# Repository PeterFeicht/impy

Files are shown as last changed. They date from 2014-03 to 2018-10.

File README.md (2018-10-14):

Bachelor's Thesis
=================

This project contains all of the stuff from my [bachelor's thesis](thesis.pdf).

The goal is to create an impedance spectrometer based on the
*Impedance Converter Network Analyzer* chip [AD5933][1] from Analog Devices.

The device uses an [STM32F4 Discovery board][2] by ST for interfacing with a PC
and MATLAB for controlling the measurement parameters.

[1]: http://www.analog.com/en/digital-to-analog-converters/direct-digital-synthesis-dds/ad5933/products/product.html
    "Analog Devices product page"
[2]: http://www.st.com/stm32f4-discovery "ST product page"
[3]: http://www.ti.com/tool/tmdssk3358 "TI product page"

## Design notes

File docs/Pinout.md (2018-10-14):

# Discovery Board Main Shield Pin Usage

This is the preliminary pin usage plan for the main shield.

Components on the main shield (most of them optional) are:

 + AD5933
 + Analog front end
 + EEPROM
 + Ethernet MAC
 + SPI Memory
 + USB A Connector

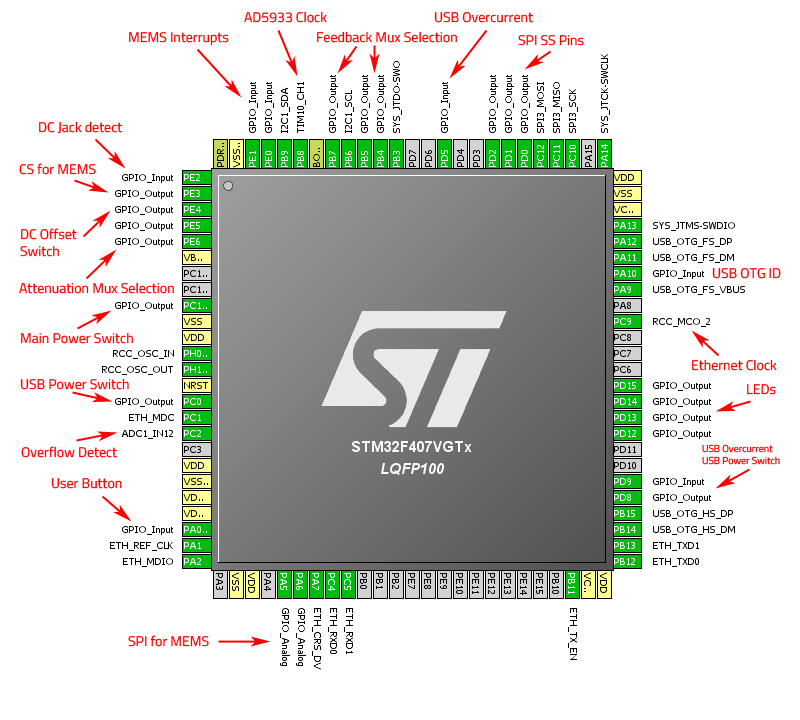
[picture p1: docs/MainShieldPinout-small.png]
Used pins for the main shield


## Pin Description:

Description of the used pins, clockwise from PE1:

| Pin(s)     | Function                  | Description                                                                 |
| ---------- | ------------------------- | --------------------------------------------------------------------------- |
| PE0/1      | MEMS Interrupt            | Unused, see [DiscoveryPins](DiscoveryPins.md).                              |
| PB9        | I2C Data                  | Used for communication with AD5933 and EEPROM.                              |
| PB8        | AD5933 Clock              | Low speed clock signal for the AD5933 for low frequency measurements.       |
| PB7        | Feedback Mux Selection    | Analog mux input selection signals, feedback resistor mux.                  |
| PB6        | I2C Clock                 | Used for communication with AD5933 and EEPROM.                              |
| PB5/4      | Feedback Mux Selection    | Analog mux input selection signals, feedback resistor mux.                  |
| PB3        | SWD Trace                 | Not used on the shield.                                                     |
| PD5        | USB Overcurrent           | Unused, see [DiscoveryPins](DiscoveryPins.md).                              |
| PD2..0     | SPI SS Pins               | Pins to be used for SPI device selection.                                   |
| PC12..PC10 | SPI Interface             | Used for SPI devices: SRAM, Flash and input Mux.                            |
| PA14/13    | SWD Clock and Data        | Not used on the shield.                                                     |
| PA12..PA9  | USB Device                | Discovery USB, not used on the shield.                                      |
| PC9        | Ethernet Clock Out        | 50MHz clock output to be used by the Ethernet MAC and STM32 ETH peripheral. |
| PD15..PD12 | LEDs                      | Discovery LEDs, not used on the shield.                                     |
| PD9        | USB Overcurrent           | Overcurrent signal for the USB host port.                                   |
| PD8        | USB Power Switch          | Output power switch enable signal for the USB host port.                    |
| PB15/14    | USB Host                  | Used for the USB A (host) connector on the shield.                          |
| PB13..PB11 | Ethernet TX               | Transmit data and enable pins for the Ethernet MAC.                         |
| PC5/4      | Ethernet RX               | Receive data pins for the Ethernet MAC.                                     |
| PA7        | Ethernet CS/DV            | Carrier Sense/Data Valid pin for the Ethernet MAC.                          |
| PA6/5      | SPI for MEMS              | Unused, see [DiscoveryPins](DiscoveryPins.md).                              |
| PA2        | Ethernet MDIO             | Management data pin for the Ethernet MAC.                                   |
| PA1        | Ethernet Clock In         | Reference clock signal input for the Ethernet MAC.                          |
| PA0        | User Button               | Discovery Button, not used on the shield.                                   |
| PC2        | Overflow Detect           | ADC input to detect possible AD5933 clipping for auto-ranging.              |
| PC1        | Ethernet MDC              | Management clock pin for the Ethernet MAC.                                  |
| PC0        | USB Power Switch          | Unused, see [DiscoveryPins](DiscoveryPins.md).                              |
| PH1/0      | Main Clock                | Main clock from the ST-LINK, not used on the shield.                        |
| PC15       | Main Power Switch         | Power switch that controls all the shield peripherals.                      |
| PE6/5      | Attenuation Mux Selection | Analog mux input selection signals, attenuation mux.                        |
| PE4        | DC Offset Switch          | Switch signal for the AD5933 output coupling capacitor.                     |
| PE3        | CS for MEMS               | Unused, see [DiscoveryPins](DiscoveryPins.md).                              |
| PE2        | DC Jack detect            | Signal from the DC Jack whether a plug is inserted.                         |

## Pin List

Alphabetical list of used pins:

| Pin(s)         | Function                  |
| -------------- | ------------------------- |
|   PA0          | User Button               |
| **PA1**        | Ethernet Clock In         |
| **PA2**        | Ethernet MDIO             |
|   PA5/6        | SPI for MEMS              |
| **PA7**        | Ethernet CS/DV            |
|   PA9..PA12    | USB Device                |
|   PA13/14      | SWD Clock and Data        |
|   PB3          | SWD Trace                 |
| **PB4/5**      | Feedback Mux Selection    |
| **PB6**        | I2C Clock                 |
| **PB7**        | Feedback Mux Selection    |
| **PB8**        | AD5933 Clock              |
| **PB9**        | I2C Data                  |
| **PB11..PB13** | Ethernet TX               |
| **PB14/15**    | USB Host                  |
|   PC0          | USB Power Switch          |
| **PC1**        | Ethernet MDC              |
| **PC2**        | Overflow Detect           |
| **PC4/5**      | Ethernet RX               |
| **PC9**        | Ethernet Clock Out        |
| **PC10..PC12** | SPI Interface             |
| **PC15**       | Main Power Switch         |
| **PD0..2**     | SPI SS Pins               |
|   PD5          | USB Overcurrent           |
| **PD8**        | USB Power Switch          |
| **PD9**        | USB Overcurrent           |
|   PD12..PD15   | LEDs                      |
|   PE0/1        | MEMS Interrupt            |
| **PE2**        | DC Jack detect            |
|   PE3          | CS for MEMS               |
| **PE4**        | DC Offset Switch          |
| **PE5/6**      | Attenuation Mux Selection |
| **PE15**       | Main Power Switch         |
|   PH0/1        | Main Clock                |

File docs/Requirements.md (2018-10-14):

Device Requirements
===================

The following lists contain some of the features the finished impedance
spectrometer needs to have or can have. This list is subject to changes as the
project progresses, but probably not much.

Must have
---------

Features the finished device must have, otherwise it can't be considered
finished:

 * PCB that plugs onto the STM32F4 Discovery board and contains the AD5933
   and peripherals.
 * Serial interface (via USB) of the AD5933 to a PC.
 * User interface in Matlab to control the device and handle the measurement data.

Nice to have
------------

Features that would be nice to have and will (more or less) likely be added to
the finished device, in order of decreasing desirability:

 * Extended measurement range of the AD5933 by means of an op-amp circuit.
 * Analog MUX on board to be able to measure multiple channels at once
   (and for calibration purposes).
 * EEPROM or similar on board to save configuration data.
 * Ethernet interface on board.
 * Additional memory on board to be able to take measurements with many points.
 * Support for multiple configurations (sweep range, voltage, etc).

Future extensions
-----------------

Features that would also be nice to have but are probably too much work to add
right away:

 * Flash memory on board to be able to save measurements on the device itself.
 * LXI compliance of the Ethernet interface.
 * Graphical user interface, either using the TI AM335x Starter Kit,
   or a display directly attached to the STM32F4.
 * USB host port to save measurements on a USB drive
   (only really useful with a GUI).

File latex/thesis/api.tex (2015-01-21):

\chapter{Programmer's Manual} \label{sec:api}

This part will be a short one, describing where programmers can start to extend the features of the device or
change the hardware configuration.
The main parts of the firmware have already been discussed in \autoref{sec:software}, so in this section
the extensible parts will be highlighted in a little more detail.

\section{Using the Virtual Console}

When writing an application that interfaces with the device (like the MATLAB scripts from \autoref{sec:matlab}),
the virtual console interface still needs to be used for device configuration.
To make non-interactive communication easier, there are two means by which the echoing of sent characters can be turned
off.

Each line that is sent can be preceded by an \texttt{@} character, thereby suppressing the echo of sent characters
for each line. This is the preferred method, since no permanent configuration is changed (which may lead to users
trying to use the device manually not seeing what they type).

The other method is to send the command \command{board set --echo=off} to turn echo off permanently. After sending
this command, no line prefix is needed (it is ignored if sent); however, to turn echo on the command has to be sent
again with \command{--echo=on}.

\section{\texttt{main.h}}

This file declares the functions provided by the main module, some of the compile-time configuration options and the
HAL peripheral handles. This is most useful when writing additional interfaces. The console module for instance uses
the functions provided by the main module to configure the sweep parameters and board settings, get the board status,
or start a sweep.

The main module provides functions directly reflecting the possible commands, like
\verb!Board_SetStartFreq(uint32_t freq)!, with a function for every command the virtual console interface accepts.
These functions also verify their arguments, so verification does not need to be implemented in every interface module.

The header file declares preprocessor constants for the GPIO ports used for the SPI peripheral.

\section{\texttt{mx\_init.c}}

This file contains the hardware initialization code. If additional peripherals need to be configured, this is the
place to add the initialization code. When additional modules are to be used, their respective HAL module needs
to be activated in \verb!stm32f4xx_hal_conf.h! as well and, when using Eclipse, the corresponding source file in
\verb!system/src/stm32f4-hal/! included in the build configuration.

The module-specific hardware configuration options (used GPIO pins, clock frequencies and the like) are mostly declared
in the header files of the modules using them.

\section{\texttt{console.h}}

This file declares the functions for the virtual console interface. It also declares a console interface structure
that is passed to the \verb!Console_ProcessLine! function, which holds pointers to functions used for communication.
This makes the console module reusable for different types of back end.

For example, both the USB VCP interface and a newly added Ethernet interface can use the virtual console module by
passing pointers to their respective communication functions. The console module then uses these pointers when it wants
to send a string or a data buffer, or when it wants to tell the back end that the current command has finished.

Currently, the callback functions for commands that do not finish immediately (calibration and temperature measurement)
are directly called from the main module. When interfaces other than the virtual console are to be added, these
calls need to be changed in order for the right interface to get a callback.

\section{Private API}

There are modules that are not supposed to be used directly by new types of interface or other extensions to the board.

The AD5933 driver module and EEPROM module header files declare the data structures used by these modules, but their
functions should not be called directly as these drivers are managed by the main module.

\subsection{EEPROM Data Structures}

However, the data structures declared in \verb!eeprom.h! may be extended when additional configuration data or settings
need to be stored on the EEPROM. The board configuration can be accessed directly by including \verb!main.h!.
For storing settings, the private functions \verb!UpdateSettings! and \verb!InitFromEEPROM! in \verb!main.c! should
be extended. A write of settings to the EEPROM can then be scheduled by calling the function \verb!MarkSettingsDirty!.

When adding additional data to the configuration and settings structures, care must be taken to adjust the size of the
\verb!reserved! fields, so the overall size of the structures does not change.

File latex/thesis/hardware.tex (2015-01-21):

\chapter{Hardware} \label{sec:hardware}

This chapter will describe the hardware design of the device.

Starting point is the \emph{AD5933} by Analog Devices, an impedance converter IC, that includes digital-to-analog and
analog-to-digital converters, a DSP engine for discrete time Fourier transform, and an internal clock source. It can
output frequencies in the desired range from \unit{10}{\hertz} to \unit{100}{\kilo\hertz} with the use of external
clock sources.

For controlling the chip and interfacing with the PC, the \emph{STM32F4 Discovery} board by ST (see \autoref{fig:stm32})
is used. This is built around an STM32F407 microcontroller, includes two USB ports (one for programming and one for use
by the microcontroller), a programmer with debugging features and a clock source, and exposes most of the microcontroller
pins on two $ 2 \times 25 $ pin headers. There are also four user programmable LEDs, as well as some other peripherals
which are not used for this project.

\begin{figure}[htpb]
  \centering
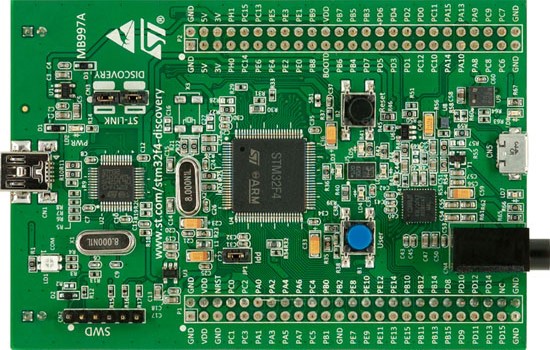
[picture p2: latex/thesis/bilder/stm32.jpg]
    
  \caption[STM32F4 Discovery board.]{STM32F4 Discovery board\footnotemark{}, USB port for debugging and programming
    on the left, USB port connected to the STM32F407 on the right.}
  \label{fig:stm32}
\end{figure}
\footnotetext{Image taken from \url{http://www.st.com/web/catalog/tools/FM116/SC959/SS1532/LN1848/PF252419}, last
  accessed 2014-12-26.}

The whole device consists of a single PCB onto which the STM32F4 Discovery board is mounted. This board has connections
for the impedances to be measured, a power supply jack, as well as a header where calibration resistors are mounted.
A picture of the front and back side of the finished board can be seen in \autoref{fig:pcb_frontback}
(\autopageref{fig:pcb_frontback}). Aside from the fitted components described later, there are footprints and traces
for a USB host connector (to save measurements onto a USB flash drive), an Ethernet jack (for remote control over
an IP network) and two additional memory chips. These features are not yet implemented in the firmware.

\begin{figure}[htpb]
  \centering
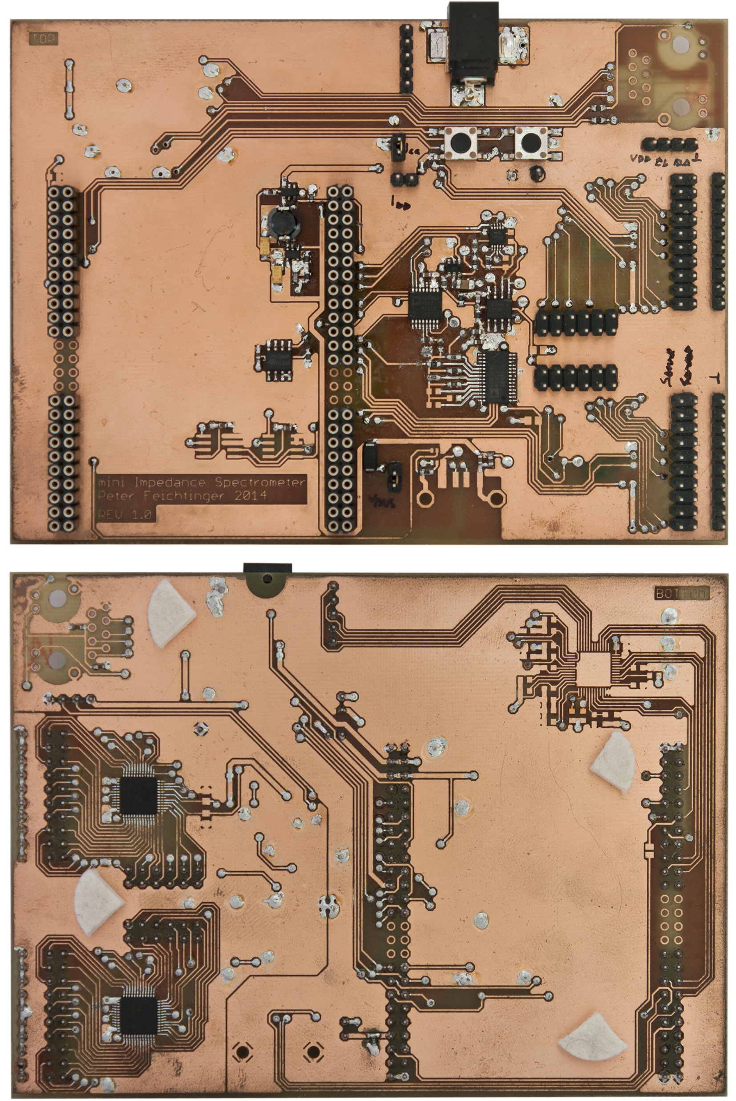
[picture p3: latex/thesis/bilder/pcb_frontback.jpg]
    
  \caption{Front (top) and back side (bottom) of the populated PCB, the STM32F4 Discovery board is mounted on the left,
    unknown impedances are connected on the right. Calibration resistors can be connected left of the measurement
    connectors.}
  \label{fig:pcb_frontback}
\end{figure}

The complete schematics for the board can be found in \autoref{sec:schematics}.

\section{The AD5933}

This section will describe the AD5933 and the impedance measurement procedure in particular, providing information
from the datasheet\footnotemark{} in a digested form.
A block diagram of the AD5933 can be seen in \autoref{fig:ad_block} (\autopageref{fig:ad_block}).
\footnotetext{Analog Devices, \enquote{1 MSPS, 12-Bit Impedance Converter, Network Analyzer,} AD5933 datasheet,
  May 2013 [Rev.\ E]: \url{http://www.analog.com/static/imported-files/data_sheets/AD5933.pdf}.}

\begin{figure}[htpb]
  \centering
    
  \caption{Block diagram of the AD5933 showing the digital and analog parts, connected to a micrcontroller
    and an impedance that is measured, respectively.}
  \label{fig:ad_block}
\end{figure}

\subsection{Measurement Procedure} \label{sec:ad5933_proc}

To measure an unknown impedance, it is excited with a known voltage at a known frequency, both of which are programmed
via the \iic{} interface.

The AD5933 DDS core generates a sine wave at a desired frequency, which is converted to analog and output by the
internal output amplifier. The output amplifier can be configured by software to different voltage levels
(approximately \unit{200}{\milli\volt}, \unit{380}{\milli\volt}, \unit{1}{\volt} or \unit{2}{\volt} peak-to-peak with
a \unit{3.3}{\volt} supply), each having a different DC offset voltage and amplifier output resistance.
The unknown impedance is connected between the output amplifier and the input amplifier. The input amplifier works as
a current-to-voltage converter and needs an external feedback resistor, which is used to set the converter ratio
and therefore influences the possible range of the unknown impedance.
The input voltage (which is proportional to the current flowing through the measured impedance) is converted to digital
after low-pass filtering and windowed for the FFT computation.
The DSP engine then calculates a Fourier transform of the input signal in relation to the output signal,
which results in the raw real and imaginary impedance values that can be read from the AD5933 registers.

Since the phase shift introduced by the system and the overall gain of the amplifiers are unknown, these values cannot
be used directly, but a calibration measurement with a known resistor needs to be made. A resistor is used because
it does not introduce a phase shift of its own.
From the calibration measurement data $ Z_\text{RAW} $, gain factor and system phase are calculated by
\begin{align}
  GF &= \left| Z_\text{RAW} \right| \cdot Z_\text{CAL} , \\
  \varphi_\text{SYS} &= \angle\, Z_\text{RAW}.
\end{align}
For an unknown impedance, the actual magnitude and phase are then calculated by
\begin{align}
  \left| Z \right| &= \frac{GF}{\left| Z_\text{RAW} \right|} , \\
  \angle\, Z &= \angle\, Z_\text{RAW} - \varphi_\text{SYS}.
\end{align}

Before starting a sweep, the AD5933 is programmed with a starting frequency, a frequency increment, the
number of increments in a sweep, and the number of settling cycles.
A sweep is then started by writing two commands to the control register, \emph{initialize with start frequency} and
\emph{start frequency sweep}. Unfortunately, the AD5933 has no interrupt capability, so the status register needs to
be queried periodically, to determine when a frequency point has been measured. The raw values are then read and an
\emph{increment frequency} or \emph{repeat frequency} command is programmed. When all points have been measured
(that is, the frequency has been incremented the set number of times), a bit in the status register is set to signal a
complete sweep.
The number of settling cycles mentioned earlier determines, how long the AD5933 waits between a change
in the output frequency and the start of the analog-to-digital conversion, giving the measured impedance time to
settle to the new frequency.

Because of the limited number of 1024 sampling points used when calculating the Fourier transform,
the frequency range with any one clock frequency is limited. Using the internal oscillator with
\unit{16.667}{\mega\hertz}, the ADC samples with \unit{1}{\mega{}S\per\second}, which limits the upper frequency to
about \unit{100}{\kilo\hertz} and the lower frequency to about \unit{1}{\kilo\hertz} to \unit{10}{\kilo\hertz}
(depending on the desired accuracy). Above \unit{100}{\kilo\hertz} the phase error increases significantly.
To measure lower frequencies, an external clock source has to be used, which is supplied by an STM32F407 timer output.
The internal clock source is used because the STM32F407 timer can only divide the \unit{120}{\mega\hertz} system clock
by integer values. This would result in either a \unit{15}{\mega\hertz} clock, which would lead to an increase in phase
error near the upper frequency limit, or a \unit{17.1}{\mega\hertz} clock, which is outside the specified range for
the AD5933 clock input.

\subsection{Analog Front End (AFE)}

The AD5933 has some severe limitations concerning its output and the load that can be placed there. Without additional
circuitry, the range is limited to at least a few \unit{100}{\kilo\ohm} up to \unit{10}{\mega\ohm}.
This limitation is caused by the significant output resistance of the output amplifier, which can be as high as
\unit{2.4}{\kilo\ohm}, as well as the output offset voltage, which limits the dynamic range of the input amplifier.

Since the desired range is down to about \unit{10}{\ohm}, and more than one impedance should be measured at once,
an external analog front end is used.
A block diagram of the external AFE can be seen in \autoref{fig:afe_block}.
There are four analog multiplexers (dual ADG725 by Analog Devices, M1 in the schematic) that connect multiple unknown
and calibration impedances in a four-wire arrangement. This allows the on-resistance of the multiplexers (which is
quite high) to be canceled out, but could also lead to signal pickup from the environment due to the high impedance
feedback path.
Multiplexer M2 is used to attenuate the output voltage of the AD5933; this is needed when measuring small impedances,
so the output current is kept small.
Multiplexer M3 switches between different feedback resistors to change the I-U conversion ratio.

\begin{figure}[hpb]
  \centering
    
  \caption{Block diagram of the AD5933 output stage with external analog front end and calibration impedance.}
  \label{fig:afe_block}
\end{figure}

The two op-amps are AD8656 by Analog Devices; the one in the output stage is configured as an inverting amplifier,
the one on the input as a current-to-voltage converter, with the AD5933-internal input amplifier acting as an inverting
voltage follower. The coupling capacitor between AD5933 output and the output amplifier filters the DC offset so the
whole input voltage range can be used.

In this configuration, the impedance range is limited by the maximum output current of the
op-amps and their closed-loop output impedance, which either needs to be small enough so it can be ignored compared
to the unknown impedance, or characterized over the whole frequency range so it can be taken into account properly.

\section{Power Supply and Memory}

Although the STM32F4 Discovery board already has a \unit{3.3}{\volt} voltage regulator that could be used, a
switching regulator (LTC3406 by Linear Technology) is included on the board. This has mainly two reasons:
\begin{itemize}
	\item for the excitation voltage of the unknown impedance to be well known, the power supply needs to be
    reasonably accurate and
  \item it should be possible to power the device from a standard USB 2.0 port, which can supply a maximum current of
    \unit{500}{\milli\ampere}. Considering that a USB host port can be added, which should in turn be able to power
    a standard USB flash drive, power conversion efficiency needs to be as high as possible. 
\end{itemize}

Since the STM32F407 does not have any non-volatile memory, an EEPROM is added to store some static configuration
options (e.g.\ fitted feedback resistors, possible output voltage attenuations or the Ethernet MAC address) as well as
dynamic settings such as the frequency range and output voltage used last. Like the AD5933, this memory is connected
via \iic{} to the microcontroller.

\section{Unpopulated Peripherals}

During the hardware design, some interesting peripherals were included in the board schematic, as well as the PCB
layout. Since programming the firmware to use these would have been beyond the scope of this thesis, they are not
populated on the final board.

These peripherals include
\begin{itemize}
  \item external SRAM and flash memory,
	\item an Ethernet jack and PHY,
  \item a USB host plug.
\end{itemize}
To populate and use them, only the respective modules need to be added to the firmware, aside from the necessary
changes, should the PCB layout turn out to be faulty.

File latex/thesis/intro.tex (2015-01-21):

\chapter{Introduction}

The goal is to develop a compact and affordable way of measuring impedance spectra. Commercially available impedance
analyzers, like the Agilent 4294A, are bulky and rather expensive devices, which are often overkill for simple
tasks, such as monitoring biological samples over many days or weeks. When the requirements for accuracy and the covered
frequency range are not very strict, such an instrument can be replaced by the simple device presented here.

The finished device is small -- it fits on a single \unit{100 \times 160}{\milli\meter} Eurocard -- and the part costs
should be somewhere around \EUR{100}.

In \autoref{sec:hardware} the hardware design as well as the AD5933 are discussed.
\hyperref[sec:software]{Chapter \ref*{sec:software}} will describe the device firmware and the MATLAB interface
functions.
\hyperref[sec:results]{Chapter \ref*{sec:results}} will cover the results from measurements with the device.
A user's manual that shows the configuration and use of the device can be found in \autoref{sec:manual}.
Finally, in \autoref{sec:api} the extensible aspects of the firmware are described in detail, to give programmers an
idea of where they need to look when developing new features.

The PCB is designed using EAGLE\footnotemark{}. The layout is somewhat convoluted because it is manufactured in-house
and holes cannot be plated through, so each connection to a through-hole pin has to be made on the bottom side.
The device can easily be assembled by hand; a soldering microscope is useful though, particularly when soldering the
TQFP48 and LQFP48 packages.

\footnotetext{EAGLE PCB Design Software available from \url{http://www.cadsoft.de/}.}

The firmware for the device is written in C using the Eclipse C Development Tools\footnotemark{}, the MATLAB interface
functions are written in MATLAB.

\footnotetext{The code is standard C11 however, so any development environment can be used.}

\section{Getting the Files}

The complete source code, the EAGLE project files, as well as the \LaTeX{} documentation are available from the project
homepage at \url{http://feichti.net/impy/}. The project can be checked out of the Subversion repository, zipped source
code packages or compiled firmware images are available on request.

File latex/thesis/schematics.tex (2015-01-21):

\chapter{Schematics} \label{sec:schematics}

The complete schematics for the board can be seen on the following pages:
\begin{itemize}
	\item \autoref{fig:schem_ad} shows AD5933 related circuitry, the external analog front end in particular.
	\item \autoref{fig:schem_power} shows power supply connections, the switching regulator and the STM32F4 Discovery
    board connectors.
	\item \autoref{fig:schem_ethernet} shows the Ethernet circuitry.
	\item \autoref{fig:schem_memory} shows the different memories.
	\item \autoref{fig:schem_misc} shows some miscellaneous things.
\end{itemize}

\begin{figure}[htpb]
  \centering
    
  \caption{Schematic for the AD5933 with external analog front end. The analog multiplexer U15 is used to charge the
    coupling capacitor to the AD5933 output offset voltage quickly.}
  \label{fig:schem_ad}
\end{figure}

\begin{figure}[htpb]
  \centering
    
  \caption{Schematics for the power supply and STM32F4 Discovery board connectors, the switching regulator and bypass
    capacitors. The two blocks U13P and U14P are power supply and SPI connections for the AFE analog multiplexers.}
  \label{fig:schem_power}
\end{figure}

\begin{figure}[htpb]
  \centering
    
  \caption{Schematic for the Ethernet interface.}
  \label{fig:schem_ethernet}
\end{figure}

\begin{figure}[htpb]
  \centering
    
  \caption{Schematics for the memories; note that there are two different footprints for the flash memory.}
  \label{fig:schem_memory}
\end{figure}

\begin{figure}[htpb]
  \centering
    
  \caption{Schematics for miscellaneous parts: an \iic{} header, pull-up resistors for the \iic{} bus, buttons, and the
    USB host jack with power switch.}
  \label{fig:schem_misc}
\end{figure}

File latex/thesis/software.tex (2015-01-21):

\chapter{Software} \label{sec:software}

This part will describe the firmware of the device and the MATLAB functions.

As mentioned in \autoref{sec:hardware}, the spectrometer is based on the \emph{STM32F4 Discovery} board, which has
an STM32F407 microcontroller and a programmer on board. On the PC side, besides an ordinary command line interface,
MATLAB can be used to control the device using some functions that are part of the provided software.

\section{Firmware}

The firmware (codename \emph{impy}) is written in C (C11) and uses the \enquote{STM32CubeF4} HAL\footnotemark{} drivers
to configure the microcontroller and control the peripherals.
\footnotetext{\textbf{H}ardware \textbf{A}bstraction \textbf{L}ayer, makes it easier to switch microcontrollers
without having to rewrite the device specific code.}
\\ It consists of four loosely coupled modules along with some support modules:
%
\begin{itemize}
	\item \verb!ad5933.c!: The AD5933 driver which takes care of communication with the AD5933 via \iic{} and collects
        the measured data.
  
  \item \verb!usbd_vcp_if.c!: The USB Virtual COM Port (VCP) interface definition, provides communication with the
        host computer.
  
  \item \verb!console.c!: Implements the virtual console that is used to control the device using a terminal
        program like \href{http://www.chiark.greenend.org.uk/~sgtatham/putty/}{PuTTY}.
  
  \item \verb!main.c!: The main module that holds the current configuration and provides an interface that is used
        by \verb!console.c! to control the basic functions of the device (e.g.\ starting a measurement, getting the
        current status, converting measured data).
\end{itemize}

Among the support modules are:
%
\begin{itemize}
	\item \verb!convert.c!: Converts measurement data to the different formats used for transfer via the USB connection.
  
  \item \verb!eeprom.c!: Used for communication with the on-board EEPROM, \verb!eeprom.h! declares the data
        structures used for storing the device configuration.
  
  \item \verb!util.c!: Provides functions for converting values (integers, IP addresses) to strings and vice versa.
  
  \item \verb!mx_init.c!: Handles the hardware initialization.
\end{itemize}

\subsection{AD5933 Driver Module}

The AD5933 driver module provides functions for managing the AD5933 and for converting raw measurement data to
meaningful values. The header files also declares the data structures used for storing measurement data and converted
values.

Since the AD5933 does not support interrupts, the driver has a timer callback function \verb!AD5933_TimerCallback(void)!
that is called by a timer interrupt handler every few milliseconds to update the driver status and collect measured
data from the AD5933. This function returns the new driver status, so appropriate action can be taken when the status
changes.

Because the AD5933 needs an external clock source to be able to measure below about \unit{10}{\kilo\hertz},
a clock signal can be output by the STM32F4 for use by the AD5933. The driver takes care of selecting the appropriate
external clock frequency to the AD5933, and of switching the external clock frequency when it needs to be changed
during a measurement.

The calibration process, needed before measurements can be made, is taken care of by the driver as well.
It is implemented to support both single-point and two-point calibration. The former only calculates an offset for one
particular frequency, whereas the latter can compensate for linear changes in the system gain and phase, by using two
frequencies and calculating an offset and a slope.
Currently, two-point calibration is always used and there is no setting to deactivate it, since the overhead is
negligible but the benefits are clear.

Besides measuring an impedance spectrum, the driver can also use the AD5933's internal temperature sensor and make a
temperature measurement. This is not terribly accurate (the AD5933 temperature sensor has a typical accuracy of
\unit{\pm 2}{\celsius}), but can be useful nonetheless.

\subsection{USB VCP Module}

The USB VCP interface pieces together a command line from characters received over the USB port and sends it to the
console module when a whole line has been received. It can be configured to echo received characters, which is useful
when typing commands by hand (otherwise one would have to type blindly), or to not echo them, which is useful when
the device is controlled by a program or script.

When a complete command is received (terminated by a newline), further input is ignored until a callback is received,
informing the interface that the command has been processed and new input should be possible.

The interface also provides functions to send single characters, strings or data buffers to the host PC.
Those are used by the console interface for feedback and for transferring measurement values.

\subsection{Console Module}

The console module takes commands assembled by the VCP interface and processes them. This is the most complicated
module, since a lot of error handling happens here.

The module has a command processing function for each top level command (see \autoref{sec:manual} for a complete
user manual), which either delegates to processing functions for sub-commands (like \texttt{board info}), or
handles the command directly (\texttt{help}, for example).

All possible commands and their arguments are defined in this file. The help text in \verb!command-line.txt!, which
is included in binary form by \verb!helptext.asm!, is processed when the console module is initialized. This makes
the help text very convenient to edit, since no C strings have to be changed but a plain text file.

All the different strings sent by the console module to the user are declared in \verb!strings_en.h!, making it easy
to change them and, if required, translate them to other languages. The language, however, can then not be changed
at run time but the firmware has to be recompiled.

\subsection{Main Module}

The main module has access to the different data buffers, keeps track of configuration changes and provides functions
to manage the commands defined by the console interface. The commands from the console interface are not handled
directly by the console module, in case other interfaces (Ethernet, for example) are also added. The different
interfaces then access the functions provided by the main module to execute the commands received.

The main module also declares the HAL handles of all microcontroller peripherals used (timers, SPI, USB, \iic{}, CRC).
The global configuration buffer that holds the hardware configuration of the board is also declared to be globally
available, so different modules can access their respective configuration data.

Hardware initialization after reset and initializing the different modules is also handled by the main module, although
the hardware part is delegated to \verb!mx_init.c!.

\subsubsection{MX Init}

\verb!mx_init.c! is less of a module on its own, but used to keep hardware initialization code out of the main file.
The code is mostly copied from files generated by \emph{STM32CubeMX}, the initialization code generation tool for the
STM32 series microcontrollers provided by ST.

The file provides a single function that handles all peripheral initialization.

\subsection{Convert Module}

The convert module provides functions to convert an array of measurement values (either raw data or polar
impedance values) to a different format for transfer; either binary or ASCII text.

The format is specified as an integer with different bits set for the desired format options.
%
\begin{description}
  \item[Binary] The only configuration options for binary transfer are the coordinate format (polar or Cartesian) and
    whether the number of bytes to follow should be sent as a header. The data format is otherwise fixed:
    \begin{itemize}
      \item Frequency: 32-bit unsigned integer
      \item Magnitude or real part: 32-bit single precision floating point
      \item Phase or imaginary part: 32-bit single precision floating point
    \end{itemize}
  
  \item[ASCII] The ASCII format has configuration options for the coordinate format, number format, whether a header
    should be printed, and how the values should be separated. Otherwise the format is similar to binary, frequency
    followed by magnitude and angle, or real and imaginary part.
\end{description}

The flags for each option are detailed in the user's manual in \autoref{sec:manual}.

\subsection{EEPROM Module}

The EEPROM module declares structures used to store the board configuration (which components are populated, values of
resistors and the like) and the current settings (frequency range, transfer format and so on). It also manages
writing and reading those structures from the EEPROM.

Since the EEPROM, like the AD5933, does not support interrupts, the driver also has a timer callback that is used when
writing data to the EEPROM. When reading data, no extra time is needed for memory access, so the timer callback is not
used then.

To prevent corruption of configuration data and settings, the EEPROM driver calculates a CRC32 checksum that is written
with the structures and verified when data is read. In addition to that, a simple algorithm for wear leveling\footnotemark{}
is implemented for the settings buffer, which is written every time settings are changed.

\footnotetext{An EEPROM degrades when written and can therefore only be written a finite number of times. When small
amounts of data are written frequently to the same address, that address will wear out quickly and make the whole
memory unusable. This can be compensated by distributing the data across the whole available memory space, thereby
reducing the number of times each address is written, a technique that is called wear leveling.}

\subsection{Util Module}

This is less of a module and more a collection of useful functions. At the moment it contains functions for parsing
MAC addresses and SI integers (numbers with an SI suffix, like 10k, for resistor or frequency values). Functions
are also provided for converting them back to string representations.

\clearpage
\section{MATLAB Interface} \label{sec:matlab}

A set of MATLAB functions is provided to make it easier for the board to be used in automated measurement setups.
The functions use the virtual console interface by sending command strings and parsing the response.
%
\begin{itemize}
	\item \verb!impy_getall!: Reads the current settings from the board and creates a MATLAB struct which can be used to
    change them.
  \item \verb!impy_setsweep!: Writes the board settings from a settings struct.
  \item \verb!impy_calibrate!: Performs a calibration with the specified resistor value, waiting for the calibration to
    complete before returning.
  \item \verb!impy_start!: Starts an impedance sweep on a specified port.
  \item \verb!impy_poll!: Used while a sweep is running to poll the board and determine when the sweep has finished.
    Returns the number of points measured when the sweep is complete.
  \item \verb!impy_read!: Reads measurement data from the board, either in polar, Cartesian, or raw format.
  \item \verb!impy_help!: Sends a help command to the board and outputs the response to the MATLAB console.
\end{itemize}

All these functions expect a COMPORT handle object that has been opened.

A sample implementation of a complete measurement cycle is provided in the file \verb!test_measure.m!; this can be used
as a starting point when using the MATLAB functions.

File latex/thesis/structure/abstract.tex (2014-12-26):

\chapter*{Abstract}

In this thesis, the construction, usage and extensibility of an impedance spectrometer based on the \emph{impedance
converter} IC AD5933 by Analog Devices are documented.

The goal is to develop a compact and affordable way of measuring impedance spectra. These are used e.g.\ 
in viscosity measurement, where a resonant sensor is used that changes its impedance characteristics depending
on the viscosity of the measured fluid. Impedance spectroscopy is also used in medical science, for example to
characterize blood or cell samples.

% German version
\begin{otherlanguage}{ngerman}
\begingroup
\let\clearpage\relax
\vspace{2cm}
\chapter*{Kurzfassung}
\endgroup

Diese Arbeit beschreibt den Aufbau, die Verwendung und die Erweiterungsmöglichkeiten eines Impedanzspektrometers rund
um den \emph{Impedance Converter} IC AD5933 von Analog Devices.

Ziel ist es, eine kompakte und kostengünstige Möglichkeit zu entwickeln um Impedanzspektren aufzunehmen. Diese
ermöglichen unter anderem die Viskositätsmessung, wo der Impedanzverlauf von resonanten Sensoren gemessen wird, der
sich in Abhängigkeit der Viskosität der gemessenen Flüssigkeit ändert. Auch im medizinischen Bereich findet die
Impedanzspektroskopie Anwendung, zum Beispiel bei der Charakterisierung von Zellen oder Blut.

\end{otherlanguage}

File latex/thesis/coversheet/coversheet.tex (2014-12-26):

%%Andreas Neubauer, Juli 2009
\documentclass[12pt,a4paper]{article}

\usepackage{graphicx,color}
\usepackage{setspace}

\textwidth 16cm
\textheight 25cm
\topmargin 3.2cm
\oddsidemargin 0mm
\parindent 0pt

\pagestyle{empty}

\begin{document}
% -------- only change entries beginning here ----------------------------
%
% enter the title of the thesis
%
\def\title{mini Impedance Spectrometer based on the AD5933}
%
%
% choose type of work: 0 ... Dissertation
%                      1 ... Diplomarbeit
%                      2 ... Masterarbeit
%                      3 ... Bachelorarbeit
\def\type{3}
%
%
% enter name of degree, see examples below
%
\def\degree{Bachelor of Science}
%\def\degree{Diplomingenieur}
%\def\degree{Diplomingenieurin}
%\def\degree{Master of Science}
%\def\degree{Doktor}
%\def\degree{Doktorin}
%
%
% enter the study (Studienrichtung)
% e.g. Diplomstudium:
%\def\study{Technische Mathematik}
% e.g. Masterstudium:
% \def\study{Industriemathematik}
% e.g. Doktorratsstudium
%\def\study{Technischen Wissenschaften}
%\def\study{Naturwissenschaften}
%
\def\study{Informationselektronik}
%
%
% enter the name of the student
%
\def\name{Peter Feichtinger}
%
%
% enter the name of the institute
% e.g.
% \def\institute{Institut f\"ur Industriemathematik}
%
\def\institute{Institut f\"ur Mikroelektronik und Mikrosensorik}
%
%
% enter the name of the supervisor (who is also the first referee)
% was also the supervisor, do so by choosing the line with (Betreuung)
%
\def\firstreferee{Univ.-Prof. Dipl.-Ing. Dr. Bernhard Jakoby}
%
%
% in case of a second referee: uncomment the following line and enter the name
%
%
\def\secondreferee{Dipl.-Ing. Stefan Clara}
%
%
% if there has been assistance by further people uncomment the following line
% and enter the name(s). if there are several assistants speerate the names by \\
%
% \def\assist{Name of assistant}
%\def\assist{Name of first assistant \\ Name of second assistant}
%
%
% enter month year
\def\date{September 2014}
%
%
% the vertival alignment heavily depends on the length of the title if there are
% one or two supervisors or referees. whereever indicated as a question
%      more space ???
% below you might add additional space via (several) \medskip or \bigskip.
% do not change anything else
% -------------------------------------------------------------------------------
%
\def\ifundefined#1{\expandafter\ifx\csname#1\endcsname\relax}
%
\unitlength 1cm
\definecolor{mygray}{gray}{.85}
\sffamily
\begin{picture}(0,0)
\put(-2.6,5){\color{mygray}\rule{25cm}{2.6cm}}
\put(10.8,5.15){\small UNIVERSIT\"AT}
\put(13.62,5.15){\small LINZ}
\put(10.8,5.5){\small JOHANNES}
\put(13,5.5){\small KEPLER}
\put(15,5.15){\Huge JKU}
\put(14.75,5.15){\line(0,1){.6}}
\put(9.7,5.6){}
\put(0,1){}
\put(3.2,1.4){\scriptsize Technisch-Naturwissenschaftliche}
\put(3.2,1.05){\scriptsize Fakult\"at}
\end{picture}
%
\begin{center}
  \begin{spacing}{1.5}
    {\LARGE\bfseries\title}
  \end{spacing}
  \vspace{3\bigskipamount}\par
  {\Large\ifcase\type DISSERTATION\or DIPLOMARBEIT\or MASTERARBEIT\or BAKKALAUREATSARBEIT\fi}
  \bigskip\par
  zur Erlangung des akademischen Grades
  \bigskip\smallskip\par
  {\Large\degree}
  \bigskip\par
  im \ifcase\type Doktoratsstudium der\or Diplomstudium\or Masterstudium\or Bachelorstudium\fi
  \bigskip\smallskip\par
  {\Large\study}
\end{center}
%
% more space ???
%\bigskip
\vspace{6\bigskipamount}\par
Eingereicht von:
\smallskip\par
{\large\name}
\medskip\bigskip\par
Angefertigt am:
\smallskip\par
{\large\institute}
\medskip\bigskip\par
Beurteilung:
\smallskip\par
{\large\firstreferee}
\smallskip\par
Betreuung:
\smallskip\par
{\large\secondreferee}
\ifundefined{assist}\else
  \medskip\bigskip\par
  Mitwirkung:
  \smallskip\par
  {\large\assist}
\fi
%
% more space ???
\vspace{5\bigskipamount}\par
{\large Linz, \date}
\end{document}

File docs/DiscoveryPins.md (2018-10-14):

# Discovery Board Pin Usage

Not all pins can be used on the discovery board, some are already connected to
peripherals on the board.

For the purpose of this project, pins connected to the audio devices and the
MEMS accelerometer are ignored, since none of those devices will be used.
However, some of them are outputs from the devices and can't be used.

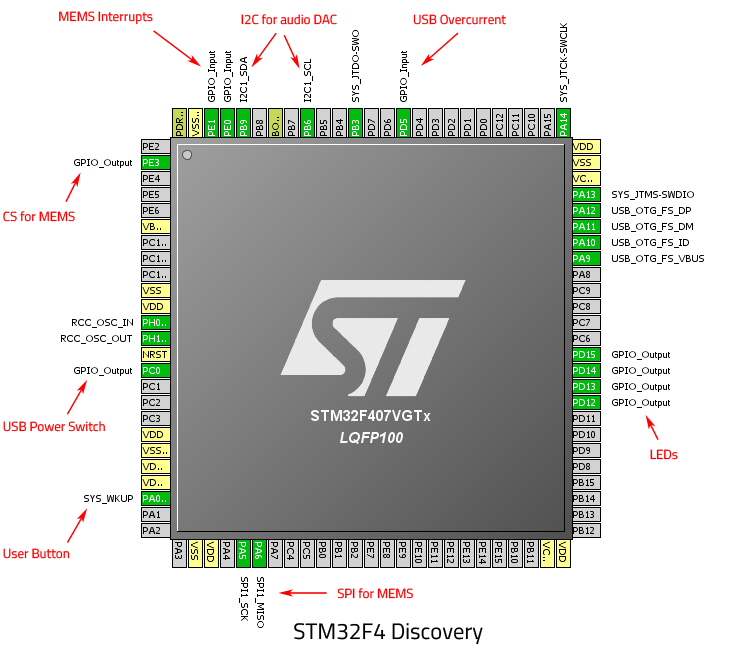
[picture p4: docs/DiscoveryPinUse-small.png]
Used pins on the STM32F4 Discovery board


## Usable pins:

| Pin(s) | Function          | Description                                                           |
| ------ | ----------------- | --------------------------------------------------------------------- |
| PB6/9  | I2C for audio DAC | I2C1 connected to the audio DAC, can be used for other stuff<br />(DAC address is `1001010 = 0x4A`, 4k7 pullup connected)               |
| PA0    | User Button       | The blue user button on the board (220k pulldown, active high)        |
| PD12   | Green LED         | Green LED to the left of the MEMS sensor                              |
| PD13   | Orange LED        | Orange LED above the MEMS sensor                                      |
| PD14   | Red LED           | Red LED to the right of the MEMS sensor                               |
| PD15   | Blue LED          | Blue LED below the MEMS sensor                                        |
| PH0/1  | HSE               | High speed oscillator in- and output (connected to 8MHz xtal + ST-LINK clock) |
| PC0    | USB Power Switch  | `!Enable` signal to the USB power supply chip (10k pullup connected)  |
| PD5    | USB Overcurrent   | `!Fault` signal from the USB power supply chip (47k pullup connected) |

## Useless pins (more or less):
| Pin(s) | Function       | Description                                                              |
| ------ | -------------- | ------------------------------------------------------------------------ |
| PE0/1  | MEMS Interrupt | Interrupt outputs from the MEMS sensor, are driven by the sensor         |
| PE3    | CS for MEMS    | SPI CS signal for the MEMS sensor (low for SPI mode, high for I2C)       |
| PA5/6  | SPI for MEMS   | PA7 could be MOSI for other SPI devices, but collides with RMII Ethernet |

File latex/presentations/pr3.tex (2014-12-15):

\documentclass{beamer}
\setbeamertemplate{navigation symbols}{} % eliminate navigation bar
\usetheme{CambridgeUS}

\usefonttheme{structurebold}
% Arch Linux Color Theme
\definecolor{arch}{RGB}{23,147,209}
\usecolortheme[named=arch]{structure}
\usecolortheme{whale}
\setbeamercolor{frametitle}{bg=arch!80!black}
\setbeamercolor{title}{bg=arch!90!black}

%% SET BEAMER TEMPLATE
%\setbeamertemplate{headline}

\usepackage{lmodern}
\usepackage{ngerman}
\usepackage[latin1]{inputenc}
\usepackage[naustrian,ngerman]{babel}

\usepackage{listings}
\lstset{basicstyle=\tiny\ttfamily,
  frame=single}
\usepackage[squaren,thinqspace,thinspace]{SIunits}

\beamersetuncovermixins{\opaqueness<1>{25}}{\opaqueness<2->{15}}

%% META INFORMATION ABOUT DOCUMENT
% \title[short]{long}
% short argument is used in places where there is little space
% long is used on the title slide

\title[Impedanzspektrometer]{mini Impedanzspektrometer mit dem AD5933}
\subtitle{Bachelorarbeit SS2014}
\institute[]{Institut für Mikroelektronik und Mikrosensorik \\ Johannes-Kepler-Universität Linz}

\subject{AD5933 Impedanzspektrometer}

% ENTER YOUR NAME, SHORT VERSION FOR FOOTER
\author[Feichtinger]{Peter Feichtinger\texorpdfstring{\\}{, } Betreuer: DI Stefan Clara} % Variante: \and

\date{16. Dezember 2014}

\begin{document}

%% TITLE PAGE
\begin{frame}
  \titlepage
\end{frame}

% for longer presentations table of contents is useful
% \begin{frame}
%    \frametitle{Outline} 
%    \tableofcontents          % optional: [pausesections]
% \end{frame}

\section{Entwicklung}  % always defined outside a frame, optional short argument
\begin{frame}[t]
  \frametitle{Einleitung}

  \begin{columns}
    \begin{column}{0.6\textwidth}
      \begin{itemize}
        \item Kompakte und preiswerte Möglichkeit zur Messung von Impedanzspektren
        \item Basierend auf dem STM32F4 Discovery Board und Analog Devices AD5933 \emph{Impedance Converter} IC
        \item Bedienung über MATLAB und virtuelle serielle Schnittstelle
      \end{itemize}
      \vspace{2cm}
    \end{column}
    
    \begin{column}{0.35\textwidth}
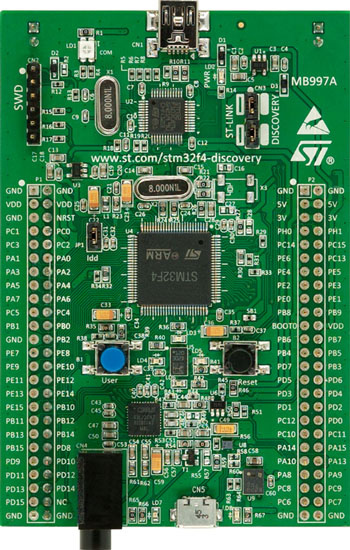
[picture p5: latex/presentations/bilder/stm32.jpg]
       \\
      \footnotesize{STM32F4 Discovery Board}
    \end{column}
  \end{columns}
\end{frame}

\begin{frame}[t]
  \frametitle{Hardware}
  
  \begin{itemize}
    \item Externes Analog-Frontend zum AD5933 mit 4-Leiter Messung
    \item Analog-Multiplexer für mehrere Ausgänge
    \item Austauschbare Kalibrierwiderstände
  \end{itemize}
  
  \vspace{1em}
  \centering
   \\
    \footnotesize{Schaltung des Analog-Frontend}
\end{frame}

\begin{frame}[t]
  \frametitle{Hardware}
  
  \begin{itemize}
    \item Größe von $ 10 \times 14 $\,cm
    \item Stromversorgung über USB oder DC-Stecker
    \item EEPROM zum Speichern von Einstellungen
  \end{itemize}
  
  \vspace{1em}
  \centering
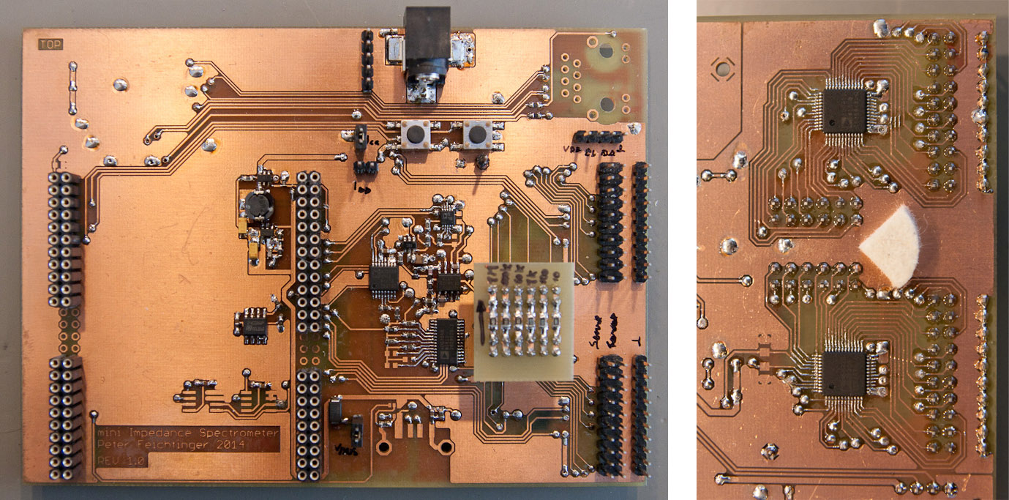
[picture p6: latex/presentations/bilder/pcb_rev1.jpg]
   \\
    \footnotesize{Erste Version der Platine}
\end{frame}

\begin{frame}[t]
	\frametitle{Firmware}
  
  \begin{itemize}
    \item Programmiert in C
    \item ST HAL Bibliothek für leichte Portierbarkeit
    \item Modularer Aufbau für gute Erweiterbarkeit
    \item Konfiguration in EEPROM gespeichert
    \begin{itemize}
      \item Aktuelle Einstellungen
      \item Bestückung von Widerständen
      \item Ethernet MAC-Adresse
    \end{itemize}
  \end{itemize}
\end{frame}

\section{Verwendung}
\begin{frame}[c,fragile=singleslide]
  \frametitle{Bedienung}
  
  \begin{columns}
    \begin{column}{0.5\textwidth}
      \begin{itemize}
        \item Konfiguration über Konsoleninterface
        \item Auslesen der Werte in verschiedenen Formaten
        \item MATLAB Funktionen zur automatisierten Steuerung
      \end{itemize}
      \vspace{2cm}
    \end{column}
    
    \begin{column}{0.45\textwidth}
      \begin{lstlisting}
board set --start=10k --stop=20k
board set --steps=10 --voltage=400
board calibrate 100
OK
board start 0
OK
board read
Frequency Magnitude Angle
10000 11.5255 1.10659
11000 14.0605 1.17955
12000 18.1948 1.13351
13000 24.6496 1.04903
14000 35.7221 0.883436
15000 54.9023 0.512685
16000 68.6387 -0.185134
17000 52.3116 -0.825151
18000 36.2655 -1.12627
19000 27.0367 -1.27099
20000 21.4698 -1.35018
      \end{lstlisting}
    \end{column}
  \end{columns}
\end{frame}

\begin{frame}[c]
  \frametitle{Ergebnisse}
  
  \begin{itemize}
    \item Gute Ergebnisse mit niedrigen ohmschen Widerständen
  \end{itemize}
  
  \centering
   \\
    \footnotesize{\unit{49.9}{\ohm} Widerstand: \unit{\pm 1}{\%} und \unit{\pm 1}{\degree}}
\end{frame}

\begin{frame}[c]
  \frametitle{Ergebnisse}
  
  \begin{itemize}
    \item Brauchbare Ergebnisse mit hohen ohmschen Widerständen
  \end{itemize}
  
  \centering
   \\
    \footnotesize{\unit{1}{\mega\ohm} Widerstand: \unit{\pm 2}{\%} und \unit{\pm 3}{\degree}}
\end{frame}

\begin{frame}[c]
  \frametitle{Ergebnisse}
  
  \begin{itemize}
    \item Unbrauchbar bei kleinen gemischten Impedanzen
  \end{itemize}
  
  \centering
   \\
    \footnotesize{Parallelschwingkreis: $ \unit{100}{\micro\henry} \,\|\, \unit{1}{\micro\farad} $}
\end{frame}

\begin{frame}[c]
  \frametitle{Verbesserungen}
  
  \begin{columns}
    \begin{column}{0.5\textwidth}
      \begin{itemize}
        \item Robusteres Analog-Frontend
        \item Autoranging implementieren
        \item Ethernet und USB Schnittstellen implementieren
        \item Genauigkeit verbessern
      \end{itemize}
      \vspace{2cm}
    \end{column}
    
    \begin{column}{0.45\textwidth}
      
    \end{column}
  \end{columns}
\end{frame}

\begin{frame}
  \centering
  Noch Fragen?
\end{frame}

\end{document}

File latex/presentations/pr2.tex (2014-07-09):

\documentclass{beamer}
\setbeamertemplate{navigation symbols}{} % eliminate navigation bar
\usetheme{CambridgeUS}

\usefonttheme{structurebold}
% Arch Linux Color Theme
\definecolor{arch}{RGB}{23,147,209}
\usecolortheme[named=arch]{structure}
\usecolortheme{whale}
\setbeamercolor{frametitle}{bg=arch!80!black}
\setbeamercolor{title}{bg=arch!90!black}

%% SET BEAMER TEMPLATE
%\setbeamertemplate{headline}

\usepackage{lmodern}
\usepackage{ngerman}
\usepackage[latin1]{inputenc}
\usepackage[naustrian,ngerman]{babel}

\usepackage{listings}
\lstset{basicstyle=\tiny\ttfamily,
  frame=single}

\beamersetuncovermixins{\opaqueness<1>{25}}{\opaqueness<2->{15}}

%% META INFORMATION ABOUT DOCUMENT
% \title[short]{long}
% short argument is used in places where there is little space
% long is used on the title slide

\title[Impedanzspektrometer]{mini Impedanzspektrometer mit dem AD5933}
\subtitle{Bachelorarbeit SS2014}
\institute[]{Institut für Mikroelektronik und Mikrosensorik \\ Johannes-Kepler-Universität Linz}

\subject{AD5933 Impedanzspektrometer}

% ENTER YOUR NAME, SHORT VERSION FOR FOOTER
\author[Feichtinger]{Peter Feichtinger\texorpdfstring{\\}{, } Betreuer: DI Stefan Clara} % Variante: \and

\date{10. Juli 2014}

\begin{document}

%% TITLE PAGE
\begin{frame}
  \titlepage
\end{frame}

% for longer presentations table of contents is useful
% \begin{frame}
%    \frametitle{Outline} 
%    \tableofcontents          % optional: [pausesections]
% \end{frame}

\section{Stand der Bachelorarbeit}  % always defined outside a frame, optional short argument
\begin{frame}[t]
  \frametitle{Hardware}
  
  \begin{itemize}
    \item Externes Analog-Frontend zum AD5933 mit 4-Leiter Messung
    \item Analog-Multiplexer für mehrere Ausgänge
    \item Austauschbare Kalibrierwiderstände
    %\item Platz für Ethernet Schnittstelle und USB-Host
  \end{itemize}
  
  \vspace{1em}
  \centering
  \only<1>{ \\
    \footnotesize{Schaltung des Analog-Frontend} }
  \only<2>{ \\
    \footnotesize{Erste Version der Platine} }
\end{frame}

% \pause can be used to uncover elements later
% doesn't work with align

% allowframebreaks, use rarely

\begin{frame}[c,fragile]
  \frametitle{Software}
  
  \begin{columns}
    \begin{column}{0.5\textwidth}
      \begin{itemize}
        \item Konfiguration über Konsoleninterface
        \item Auslesen der Werte in verschiedenen Formaten
        \item MATLAB Funktionen zur automatisierten Steuerung
      \end{itemize}
      \vspace{2cm}
    \end{column}
    
    \begin{column}{0.45\textwidth}
      \begin{lstlisting}
board set --start=10k --stop=20k
board set --steps=10 --voltage=400
board calibrate 100
OK
board start 0
OK
board read
Frequency Magnitude Angle
10000 11.5255 1.10659
11000 14.0605 1.17955
12000 18.1948 1.13351
13000 24.6496 1.04903
14000 35.7221 0.883436
15000 54.9023 0.512685
16000 68.6387 -0.185134
17000 52.3116 -0.825151
18000 36.2655 -1.12627
19000 27.0367 -1.27099
20000 21.4698 -1.35018
      \end{lstlisting}
    \end{column}
  \end{columns}
\end{frame}

\begin{frame}[c]
  \frametitle{Ausblick}
  
  \begin{columns}
    \begin{column}{0.5\textwidth}
      \begin{itemize}
        \item Robusteres Analog-Frontend
        \item Vergleichsmessungen mit Agilent 4294A
        \item Genauigkeit untersuchen
        \item Autoranging und Ethernet Schnittstelle implementieren
      \end{itemize}
      \vspace{2cm}
    \end{column}
    
    \begin{column}{0.45\textwidth}
      
    \end{column}
  \end{columns}
\end{frame}

%\begin{frame}
  %\centering
  %Vielen Dank für Ihre Aufmerksamkeit!
%\end{frame}

\end{document}

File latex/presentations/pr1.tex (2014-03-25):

\documentclass{beamer}
\setbeamertemplate{navigation symbols}{} % eliminate navigation bar
\usetheme{CambridgeUS}

\usefonttheme{structurebold}
% Arch Linux Color Theme
\definecolor{arch}{RGB}{23,147,209}
\usecolortheme[named=arch]{structure}
\usecolortheme{whale}
\setbeamercolor{frametitle}{bg=arch!80!black}
\setbeamercolor{title}{bg=arch!90!black}

%% SET BEAMER TEMPLATE
%\setbeamertemplate{headline}

\usepackage{lmodern}
\usepackage{ngerman}
\usepackage[latin1]{inputenc}
\usepackage[naustrian,ngerman]{babel}

\beamersetuncovermixins{\opaqueness<1>{25}}{\opaqueness<2->{15}}

%% META INFORMATION ABOUT DOCUMENT
% \title[short]{long}
% short argument is used in places where there is little space
% long is used on the title slide

\title[Impedanzspektrometer]{Bau eines Impedanzspektrometers mit dem AD5933}
\subtitle{Bachelorarbeit SS2014}
\institute[]{Institut für Mikroelektronik und Mikrosensorik \\ Johannes-Kepler-Universität Linz}

\subject{AD5933 Impedanzspektrometer}

% ENTER YOUR NAME, SHORT VERSION FOR FOOTER
\author[Feichtinger]{Peter Feichtinger\texorpdfstring{\\}{, } Betreuer: DI Stefan Clara} % Variante: \and

\date{19. März 2014}

\begin{document}

%% TITLE PAGE
\begin{frame}
  \titlepage
\end{frame}

% for longer presentations table of contents is useful
% \begin{frame}
%    \frametitle{Outline} 
%    \tableofcontents          % optional: [pausesections]
% \end{frame}

\section{Thema der Bachelorarbeit}  % always defined outside a frame, optional short argument
\begin{frame}[t]
  \frametitle{Aufgabenstellung}

  \begin{columns}
    \begin{column}{0.6\textwidth}
      \begin{itemize}
        \item Erweiterungsmöglichkeiten des AD5933 analysieren
        \item Entwurf und Realisierung einer Schaltung
        \item Verbindung zum PC mittels STM32F4 Discovery Board und Auswertung in MATLAB
        \item Eventuell eigene Ethernet Schnittstelle
      \end{itemize}
      \vspace{3cm}
    \end{column}
    
    \begin{column}{0.35\textwidth}
       \\
      \footnotesize{STM32F4 Discovery Board}
    \end{column}
  \end{columns}
\end{frame}

% \pause can be used to uncover elements later
% doesn't work with align

% allowframebreaks, use rarely

\begin{frame}[t]
  \frametitle{AD5933 Impedance Converter Network Analyzer}

  \begin{itemize}
    \item Ansteuerung per $ I^2C $
    \item Liefert Real- und Imaginärteil der Impedanz
    \item Einfache Aufnahme des Frequenzgangs
  \end{itemize}
  
  \vspace{1em}
  \centering
     \\
  \footnotesize{AD5933 Blockschaltbild}
\end{frame}

\begin{frame}[t]
  \frametitle{Mögliche Erweiterung}
  
  \begin{itemize}
    \item Eigenständige Benutzeroberfläche mit TI AM335x Starter Kit
    \item Netzwerkanbindung per Ethernet oder WLAN
    \item Export der Daten auf USB-Stick
  \end{itemize}
  
  \vspace{1em}
  \centering
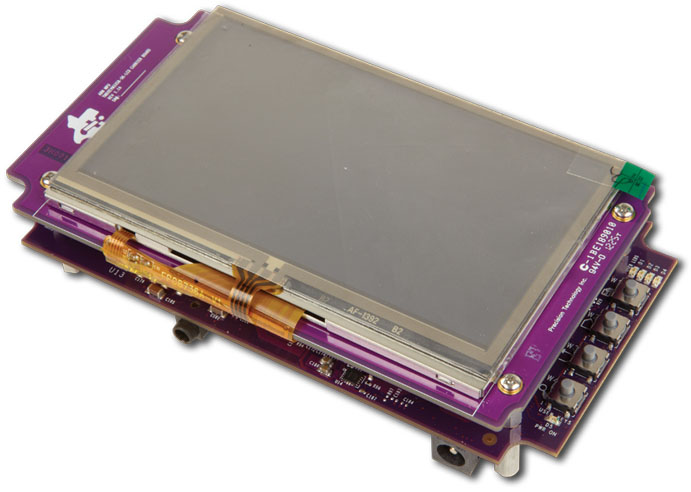
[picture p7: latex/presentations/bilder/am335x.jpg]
     \\
  \footnotesize{AM335x Starter Kit}
\end{frame}

%\begin{frame}
  %\centering
  %Vielen Dank für Ihre Aufmerksamkeit!
%\end{frame}

\end{document}

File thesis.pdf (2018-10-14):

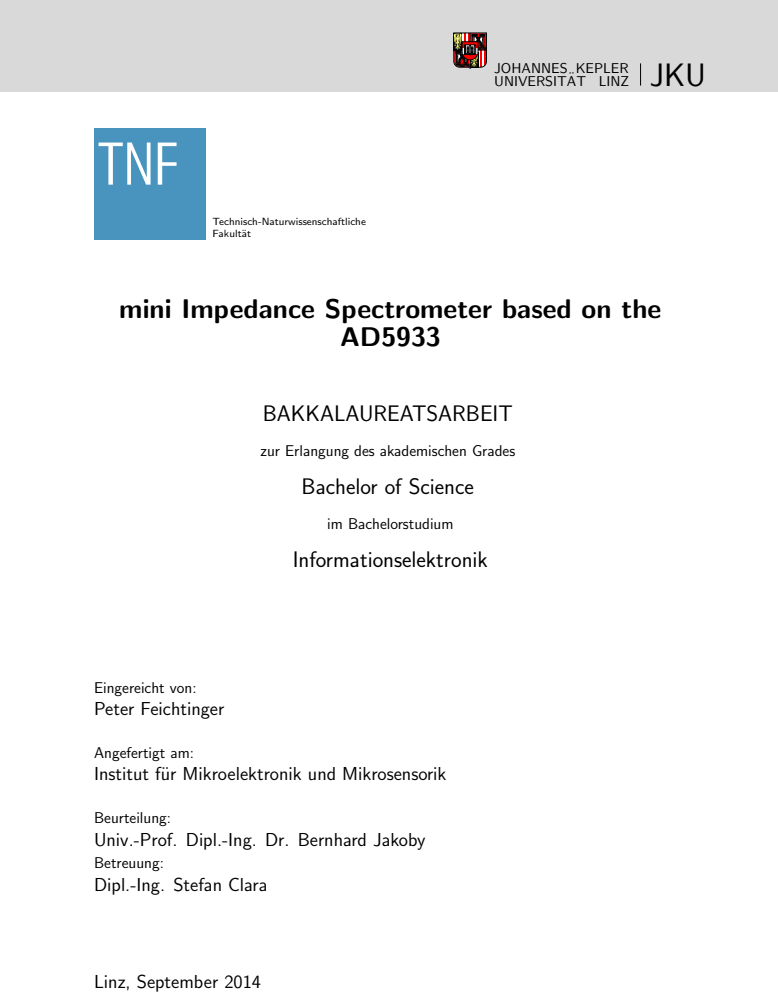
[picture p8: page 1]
UNIVERSITAT LINZ ¨; JOHANNES KEPLER; JKU; Technisch-Naturwissenschaftliche Fakult¨at; BAKKALAUREATSARBEIT; im Bachelorstudium Informationselektronik; Eingereicht von: Peter Feichtinger; Linz, September 2014

mini Impedance Spectrometer based on the

zur Erlangung des akademischen Grades
Bachelor of Science

Angefertigt am:
Institut f¨ur Mikroelektronik und Mikrosensorik

Beurteilung:
Univ.-Prof. Dipl.-Ing. Dr. Bernhard Jakoby
Betreuung:
Dipl.-Ing. Stefan Clara

iii

# Abstract

In this thesis, the construction, usage and extensibility of an impedance spectrometer based on the impedance converter IC AD5933 by Analog Devices are documented.

The goal is to develop a compact and affordable way of measuring impedance spectra. These are used e.g. in viscosity measurement, where a resonant sensor is used that changes its impedance characteristics depending on the viscosity of the measured fluid. Impedance spectroscopy is also used in medical science, for example to characterize blood or cell samples.

# Kurzfassung

Diese Arbeit beschreibt den Aufbau, die Verwendung und die Erweiterungsmöglichkeiten eines Impedanzspektrometers rund um den Impedance Converter IC AD5933 von Analog Devices.

Ziel ist es, eine kompakte und kostengünstige Möglichkeit zu entwickeln um Impedanzspektren aufzunehmen. Diese ermöglichen unter anderem die Viskositätsmessung, wo der Impedanzverlauf von resonanten Sensoren gemessen wird, der sich in Abhängigkeit der Viskosität der gemessenen Flüssigkeit ändert. Auch im medizinischen Bereich findet die Impedanzspektroskopie Anwendung, zum Beispiel bei der Charakterisierung von Zellen oder Blut.

CONTENTS | v

# Contents

1 Introduction | 1
2 Hardware | 3
3 Software | 11
4 Results | 17
5 User’s Manual | 21

vi | CONTENTS
6 Programmer’s Manual | 31
A Schematics | 35
Acknowledgment | 41
Eidesstattliche Erklärung | 43

1

# 1 Introduction

The goal is to develop a compact and affordable way of measuring impedance spectra. Commercially available impedance analyzers, like the Agilent 4294A, are bulky and rather expensive devices, which are often overkill for simple tasks, such as monitoring biological samples over many days or weeks. When the requirements for accuracy and the covered frequency range are not very strict, such an instrument can be replaced by the simple device presented here.

The finished device is small – it fits on a single 100 × 160 mm Eurocard – and the part costs should be somewhere around 100 e.

In chapter 2 the hardware design as well as the AD5933 are discussed. Chapter 3 will describe the device firmware and the MATLAB interface functions. Chapter 4 will cover the results from measurements with the device. A user’s manual that shows the configuration and use of the device can be found in chapter 5. Finally, in chapter 6 the extensible aspects of the firmware are described in detail, to give programmers an idea of where they need to look when developing new features.

The PCB is designed using EAGLE¹
. The layout is somewhat convoluted because it is manufactured in-house and holes cannot be plated through, so each connection to a through-hole pin has to be made on the bottom side. The device can easily be assembled by hand; a soldering microscope is useful though, particularly when soldering the TQFP48 and LQFP48 packages.

The firmware for the device is written in C using the Eclipse C Development Tools² ,
the MATLAB interface functions are written in MATLAB.

## 1.1 Getting the Files

The complete source code, the EAGLE project files, as well as the LATEX documentation are available from the project homepage at http://feichti.net/impy/. The project can be checked out of the Subversion repository, zipped source code packages or compiled firmware images are available on request.

1EAGLE PCB Design Software available from http://www.cadsoft.de/.
2The code is standard C11 however, so any development environment can be used.

3

# 2 Hardware

This chapter will describe the hardware design of the device.

Starting point is the AD5933 by Analog Devices, an impedance converter IC, that includes digital-to-analog and analog-to-digital converters, a DSP engine for discrete time Fourier transform, and an internal clock source. It can output frequencies in the desired range from 10 Hz to 100 kHz with the use of external clock sources.

For controlling the chip and interfacing with the PC, the STM32F4 Discovery board by ST (see Figure 2.1) is used. This is built around an STM32F407 microcontroller, includes two USB ports (one for programming and one for use by the microcontroller), a programmer with debugging features and a clock source, and exposes most of the microcontroller pins on two 2 × 25 pin headers. There are also four user

programmable LEDs, as well as some other peripherals which are not used for this project.


Figure 2.1: STM32F4 Discovery board¹
, USB port for debugging and programming on the left, USB port connected to the STM32F407 on the right.

The whole device consists of a single PCB onto which the STM32F4 Discovery board is mounted. This board has connections for the impedances to be measured, a power supply jack, as well as a header where calibration resistors are mounted. A picture of the front and back side of the finished board can be seen in Figure 2.2 (page 5).

1
Image taken from http://www.st.com/web/catalog/tools/FM116/SC959/SS1532/LN1848/PF252419, (http://www.st.com/web/catalog/tools/FM116/SC959/SS1532/LN1848/PF252419) last accessed 2014-12-26.

4 | 2. HARDWARE

Aside from the fitted components described later, there are footprints and traces for a USB host connector (to save measurements onto a USB flash drive), an Ethernet jack (for remote control over an IP network) and two additional memory chips.

These features are not yet implemented in the firmware.

The complete schematics for the board can be found in Appendix A.

## 2.1 The AD5933

This section will describe the AD5933 and the impedance measurement procedure in particular, providing information from the datasheet²
in a digested form. A block diagram of the AD5933 can be seen in Figure 2.3 (page 6).

### 2.1.1 Measurement Procedure

To measure an unknown impedance, it is excited with a known voltage at a known frequency, both of which are programmed via the I²C interface.

The AD5933 DDS core generates a sine wave at a desired frequency, which is converted to analog and output by the internal output amplifier. The output amplifier can be configured by software to different voltage levels (approximately 200 mV, 380 mV, 1 V or 2 V peak-to-peak with a 3.3 V supply), each having a different DC

offset voltage and amplifier output resistance. The unknown impedance is connected between the output amplifier and the input amplifier. The input amplifier works as a current-to-voltage converter and needs an external feedback resistor, which is used to set the converter ratio and therefore influences the possible range of the unknown impedance. The input voltage (which is proportional to the current flowing through the measured impedance) is converted to digital after low-pass filtering

and windowed for the FFT computation. The DSP engine then calculates a Fourier transform of the input signal in relation to the output signal, which results in the raw real and imaginary impedance values that can be read from the AD5933 registers.

Since the phase shift introduced by the system and the overall gain of the amplifiers are unknown, these values cannot be used directly, but a calibration measurement with a known resistor needs to be made. A resistor is used because it does not introduce a phase shift of its own. From the calibration measurement data ZRAW, gain factor and system phase are calculated by

GF = |ZRAW| ·ZCAL, | (2.1)
ϕSYS = ∠ ZRAW. | (2.2)

2Analog Devices, “1 MSPS, 12-Bit Impedance Converter, Network Analyzer,” AD5933 datasheet, May 2013 [Rev. E]: http://www.analog.com/static/imported-files/data_sheets/AD5933.pdf.

2.1. THE AD5933 | 5


Figure 2.2: Front (top) and back side (bottom) of the populated PCB, the STM32F4 Discovery board is mounted on the left, unknown impedances are connected on the right. Calibration resistors can be connected left of the measurement connectors.

6 | 2. HARDWARE

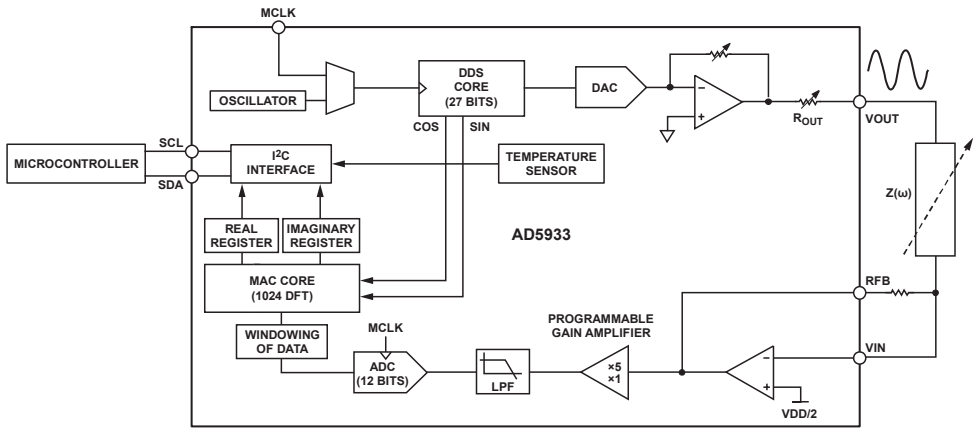
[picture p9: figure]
ADC (12 BITS); VDD/2; DDS CORE (27 BITS); DAC; I²C INTERFACE; IMAGINARY REGISTER; REAL REGISTER; MAC CORE (1024 DFT); LPF; SCL; SDA; MCLK; ROUT; VOUT; RFB; VIN; PROGRAMMABLE GAIN AMPLIFIER; WINDOWING OF DATA; COS; SIN; MICROCONTROLLER; TEMPERATURE SENSOR; OSCILLATOR

Figure 2.3: Block diagram of the AD5933 showing the digital and analog parts, connected to a micrcontroller and an impedance that is measured, respectively.

For an unknown impedance, the actual magnitude and phase are then calculated by

|Z| =

GF

|ZRAW|

, | (2.3)
∠ Z = ∠ ZRAW − ϕSYS. | (2.4)

Before starting a sweep, the AD5933 is programmed with a starting frequency, a frequency increment, the number of increments in a sweep, and the number of settling cycles. A sweep is then started by writing two commands to the control register, initialize with start frequency and start frequency sweep. Unfortunately, the AD5933

has no interrupt capability, so the status register needs to be queried periodically, to determine when a frequency point has been measured. The raw values are then read and an increment frequency or repeat frequency command is programmed. When all points have been measured (that is, the frequency has been incremented the set number of times), a bit in the status register is set to signal a complete sweep. The

number of settling cycles mentioned earlier determines, how long the AD5933 waits between a change in the output frequency and the start of the analog-to-digital conversion, giving the measured impedance time to settle to the new frequency.

Because of the limited number of 1024 sampling points used when calculating the Fourier transform, the frequency range with any one clock frequency is limited. Using the internal oscillator with 16.667 MHz, the ADC samples with 1 MS/s, which

limits the upper frequency to about 100 kHz and the lower frequency to about 1 kHz to 10 kHz (depending on the desired accuracy). Above 100 kHz the phase error

increases significantly. To measure lower frequencies, an external clock source has to be used, which is supplied by an STM32F407 timer output. The internal clock source is used because the STM32F407 timer can only divide the 120 MHz system

2.1. THE AD5933 | 7

clock by integer values. This would result in either a 15 MHz clock, which would lead to an increase in phase error near the upper frequency limit, or a 17.1 MHz clock, which is outside the specified range for the AD5933 clock input.

### 2.1.2 Analog Front End (AFE)

The AD5933 has some severe limitations concerning its output and the load that can be placed there. Without additional circuitry, the range is limited to at least a few 100 kΩ up to 10 MΩ. This limitation is caused by the significant output resistance of the output amplifier, which can be as high as 2.4 kΩ, as well as the output offset voltage, which limits the dynamic range of the input amplifier.

Since the desired range is down to about 10 Ω, and more than one impedance should be measured at once, an external analog front end is used. A block diagram of the external AFE can be seen in Figure 2.4. There are four analog multiplexers (dual ADG725 by Analog Devices, M1 in the schematic) that connect multiple unknown

and calibration impedances in a four-wire arrangement. This allows the on-resistance of the multiplexers (which is quite high) to be canceled out, but could also lead

to signal pickup from the environment due to the high impedance feedback path. Multiplexer M2 is used to attenuate the output voltage of the AD5933; this is needed

when measuring small impedances, so the output current is kept small. Multiplexer M3 switches between different feedback resistors to change the I-U conversion ratio.

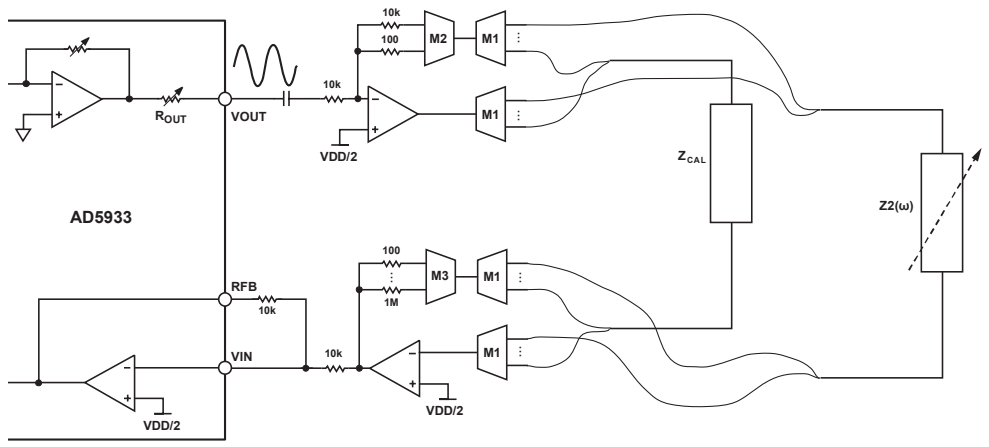
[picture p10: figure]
VDD/2; ROUT; VOUT; RFB; VIN; ZCAL

Figure 2.4: Block diagram of the AD5933 output stage with external analog front end and calibration impedance.

The two op-amps are AD8656 by Analog Devices; the one in the output stage is configured as an inverting amplifier, the one on the input as a current-to-voltage converter, with the AD5933-internal input amplifier acting as an inverting voltage

8 | 2. HARDWARE

follower. The coupling capacitor between AD5933 output and the output amplifier filters the DC offset so the whole input voltage range can be used.

In this configuration, the impedance range is limited by the maximum output current of the op-amps and their closed-loop output impedance, which either needs to be small enough so it can be ignored compared to the unknown impedance, or characterized over the whole frequency range so it can be taken into account properly.

## 2.2 Power Supply and Memory

Although the STM32F4 Discovery board already has a 3.3 V voltage regulator that could be used, a switching regulator (LTC3406 by Linear Technology) is included

on the board. This has mainly two reasons:

- for the excitation voltage of the unknown impedance to be well known, the

power supply needs to be reasonably accurate and

- it should be possible to power the device from a standard USB 2.0 port, which

can supply a maximum current of 500 mA. Considering that a USB host port can be added, which should in turn be able to power a standard USB flash drive, power conversion efficiency needs to be as high as possible.

Since the STM32F407 does not have any non-volatile memory, an EEPROM is added to store some static configuration options (e.g. fitted feedback resistors, possible output voltage attenuations or the Ethernet MAC address) as well as dynamic settings

such as the frequency range and output voltage used last. Like the AD5933, this memory is connected via I²C to the microcontroller.

## 2.3 Unpopulated Peripherals

During the hardware design, some interesting peripherals were included in the board schematic, as well as the PCB layout. Since programming the firmware to use these would have been beyond the scope of this thesis, they are not populated on the final board.

These peripherals include

- external SRAM and flash memory,
- an Ethernet jack and PHY,
- a USB host plug.

2.3. UNPOPULATED PERIPHERALS | 9

To populate and use them, only the respective modules need to be added to the firmware, aside from the necessary changes, should the PCB layout turn out to be faulty.

11

# 3 Software

This part will describe the firmware of the device and the MATLAB functions.

As mentioned in chapter 2, the spectrometer is based on the STM32F4 Discovery board, which has an STM32F407 microcontroller and a programmer on board. On the PC side, besides an ordinary command line interface, MATLAB can be used to control the device using some functions that are part of the provided software.

## 3.1 Firmware

The firmware (codename impy) is written in C (C11) and uses the “STM32CubeF4” HAL¹ drivers to configure the microcontroller and control the peripherals.

It consists of four loosely coupled modules along with some support modules:

- ad5933.c: The AD5933 driver which takes care of communication with the AD5933 via I²C and collects the measured data.
- usbd_vcp_if.c: The USB Virtual COM Port (VCP) interface definition, pro-

vides communication with the host computer.

- console.c: Implements the virtual console that is used to control the device

using a terminal program like PuTTY. (http://www.chiark.greenend.org.uk/~sgtatham/putty/)

- main.c: The main module that holds the current configuration and provides

an interface that is used by console.c to control the basic functions of the device (e.g. starting a measurement, getting the current status, converting measured data).

Among the support modules are:

- convert.c: Converts measurement data to the different formats used for

transfer via the USB connection.

- eeprom.c: Used for communication with the on-board EEPROM, eeprom.h

declares the data structures used for storing the device configuration.

1Hardware Abstraction Layer, makes it easier to switch microcontrollers without having to rewrite the device specific code.

12 | 3. SOFTWARE
- util.c: Provides functions for converting values (integers, IP addresses) to

strings and vice versa.

- mx_init.c: Handles the hardware initialization.

### 3.1.1 AD5933 Driver Module

The AD5933 driver module provides functions for managing the AD5933 and for converting raw measurement data to meaningful values. The header files also declares the data structures used for storing measurement data and converted values.

Since the AD5933 does not support interrupts, the driver has a timer callback func-

tion AD5933_TimerCallback(void) that is called by a timer interrupt handler every few milliseconds to update the driver status and collect measured data from the AD5933. This function returns the new driver status, so appropriate action can be

taken when the status changes.

Because the AD5933 needs an external clock source to be able to measure below about 10 kHz, a clock signal can be output by the STM32F4 for use by the AD5933. The driver takes care of selecting the appropriate external clock frequency to the AD5933, and of switching the external clock frequency when it needs to be changed

during a measurement.

The calibration process, needed before measurements can be made, is taken care of by the driver as well. It is implemented to support both single-point and two-point calibration. The former only calculates an offset for one particular frequency, whereas the latter can compensate for linear changes in the system gain and phase, by using two frequencies and calculating an offset and a slope. Currently, two-point calibration is always used and there is no setting to deactivate it, since the overhead is negligible but the benefits are clear.

Besides measuring an impedance spectrum, the driver can also use the AD5933’s

internal temperature sensor and make a temperature measurement. This is not terribly accurate (the AD5933 temperature sensor has a typical accuracy of ±2

◦C),

but can be useful nonetheless.

### 3.1.2 USB VCP Module

The USB VCP interface pieces together a command line from characters received over the USB port and sends it to the console module when a whole line has been received. It can be configured to echo received characters, which is useful when typing commands by hand (otherwise one would have to type blindly), or to not

echo them, which is useful when the device is controlled by a program or script.

3.1. FIRMWARE | 13

When a complete command is received (terminated by a newline), further input is

ignored until a callback is received, informing the interface that the command has been processed and new input should be possible.

The interface also provides functions to send single characters, strings or data buffers to the host PC. Those are used by the console interface for feedback and for transferring measurement values.

### 3.1.3 Console Module

The console module takes commands assembled by the VCP interface and processes them. This is the most complicated module, since a lot of error handling happens here.

The module has a command processing function for each top level command (see chapter 5 for a complete user manual), which either delegates to processing functions for sub-commands (like board info), or handles the command directly (help, for example).

All possible commands and their arguments are defined in this file. The help text in command-line.txt, which is included in binary form by helptext.asm, is processed when the console module is initialized. This makes the help text very convenient to edit, since no C strings have to be changed but a plain text file.

All the different strings sent by the console module to the user are declared in strings_en.h, making it easy to change them and, if required, translate them to other languages. The language, however, can then not be changed at run time but the firmware has to be recompiled.

### 3.1.4 Main Module

The main module has access to the different data buffers, keeps track of configuration changes and provides functions to manage the commands defined by the console interface. The commands from the console interface are not handled directly by the console module, in case other interfaces (Ethernet, for example) are also added.

The different interfaces then access the functions provided by the main module to execute the commands received.

The main module also declares the HAL handles of all microcontroller peripherals used (timers, SPI, USB, I²C, CRC). The global configuration buffer that holds the

hardware configuration of the board is also declared to be globally available, so different modules can access their respective configuration data.

Hardware initialization after reset and initializing the different modules is also handled by the main module, although the hardware part is delegated to mx_init.c.

14 | 3. SOFTWARE

MX Init

mx_init.c is less of a module on its own, but used to keep hardware initialization code out of the main file. The code is mostly copied from files generated by STM32CubeMX, the initialization code generation tool for the STM32 series microcontrollers provided by ST.

The file provides a single function that handles all peripheral initialization.

### 3.1.5 Convert Module

The convert module provides functions to convert an array of measurement values (either raw data or polar impedance values) to a different format for transfer; either

binary or ASCII text.

The format is specified as an integer with different bits set for the desired format options.

Binary The only configuration options for binary transfer are the coordinate format (polar or Cartesian) and whether the number of bytes to follow should be

sent as a header. The data format is otherwise fixed:

- Frequency: 32-bit unsigned integer
- Magnitude or real part: 32-bit single precision floating point
- Phase or imaginary part: 32-bit single precision floating point

ASCII The ASCII format has configuration options for the coordinate format, number format, whether a header should be printed, and how the values should be separated. Otherwise the format is similar to binary, frequency followed by magnitude and angle, or real and imaginary part.

The flags for each option are detailed in the user’s manual in chapter 5.

### 3.1.6 EEPROM Module

The EEPROM module declares structures used to store the board configuration (which components are populated, values of resistors and the like) and the current settings (frequency range, transfer format and so on). It also manages writing and

reading those structures from the EEPROM.

Since the EEPROM, like the AD5933, does not support interrupts, the driver also has a timer callback that is used when writing data to the EEPROM. When reading data, no extra time is needed for memory access, so the timer callback is not used then.

3.1. FIRMWARE | 15

To prevent corruption of configuration data and settings, the EEPROM driver calculates a CRC32 checksum that is written with the structures and verified when data is read. In addition to that, a simple algorithm for wear leveling²
is implemented
for the settings buffer, which is written every time settings are changed.

### 3.1.7 Util Module

This is less of a module and more a collection of useful functions. At the moment it contains functions for parsing MAC addresses and SI integers (numbers with an SI suffix, like 10k, for resistor or frequency values). Functions are also provided for

converting them back to string representations.

2An EEPROM degrades when written and can therefore only be written a finite number of times. When small amounts of data are written frequently to the same address, that address will wear out quickly and make the whole memory unusable. This can be compensated by distributing the data across the whole available memory space, thereby reducing the number of times each address is written, a technique that is called wear leveling.

16 | 3. SOFTWARE

## 3.2 MATLAB Interface

A set of MATLAB functions is provided to make it easier for the board to be used in automated measurement setups. The functions use the virtual console interface by sending command strings and parsing the response.

- impy_getall: Reads the current settings from the board and creates a MAT-

LAB struct which can be used to change them.

- impy_setsweep: Writes the board settings from a settings struct.
- impy_calibrate: Performs a calibration with the specified resistor value, wait-

ing for the calibration to complete before returning.

- impy_start: Starts an impedance sweep on a specified port.
- impy_poll: Used while a sweep is running to poll the board and determine

when the sweep has finished. Returns the number of points measured when the sweep is complete.

- impy_read: Reads measurement data from the board, either in polar, Carte-

sian, or raw format.

- impy_help: Sends a help command to the board and outputs the response to

the MATLAB console.

All these functions expect a COMPORT handle object that has been opened.

A sample implementation of a complete measurement cycle is provided in the file test_measure.m; this can be used as a starting point when using the MATLAB functions.

17

# 4 Results

The performance of the device was analyzed by measuring some resistors and other mixed networks.

With small resistors in the range of a few 10 Ω to 10 kΩ, the accuracy is better than 1 %. Figure 4.1 shows a measurement of a 49.9 Ω resistor, Figure 4.2 shows the

results with a 5.6 kΩ resistor and Figure 4.3 the results with a 10 kΩ resistor. Every profile is well within the ±1 % range, the impedance angle is close to 0, as would be

expected from an ohmic resistor.

For resistors of larger magnitude, the accuracy is not as good; a measurement of a 1 MΩ resistor can be seen in Figure 4.4. There are non-linear terms in the system gain that are not compensated by the two-point calibration, which result in the nonlinear impedance profile. The measured angle shows a linear trend, which should be compensated by the two-point calibration but is not. Also note the change in slope and noise at 10 kHz, where the clock source is switched from the external source below 10 kHz to the internal one above.

When sweeping over larger frequency ranges, the accuracy is not as good, especially in the range near or above 100 kHz. In general, it is advisable to use a frequency range as narrow as possible, since the two-point calibration can only account for constant and linear terms in the system gain. Nonlinearities however only manifest when a large frequency range is swept all at once.

For small mixed impedance networks, however, the results are quite bad. Because of an instability in the external AFE, the measurement results cannot be used at all. Figure 4.5 shows a measurement of a high-Q LC resonant circuit, as can be seen the impedance value as well as the resonant frequency of the circuit are way off. A similar LC circuit with a lower Q-factor shows better results (compare Figure 4.6),

the accuracy is not good enough nonetheless.

A goal for further work on the device is to replace the current topology of the external analog front end (inverting amplifier configured as an attenuator on the output, current to voltage conversion on the input) by a different one. A possible

approach is to use a current source on the output and directly measure the voltage across the impedance on the input.

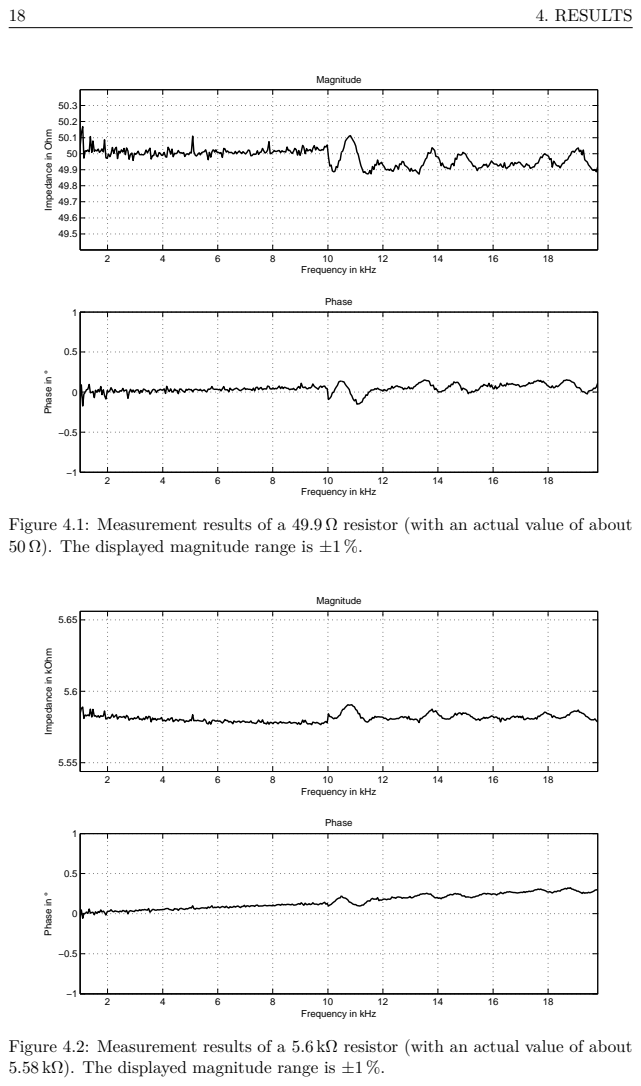
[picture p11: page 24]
4. RESULTS; Magnitude; Phase in °; Phase

Impedance in Ohm

Frequency in kHz

Figure 4.1: Measurement results of a 49.9 Ω resistor (with an actual value of about
50 Ω). The displayed magnitude range is ±1 %.

Impedance in kOhm

Figure 4.2: Measurement results of a 5.6 kΩ resistor (with an actual value of about
5.58 kΩ). The displayed magnitude range is ±1 %.

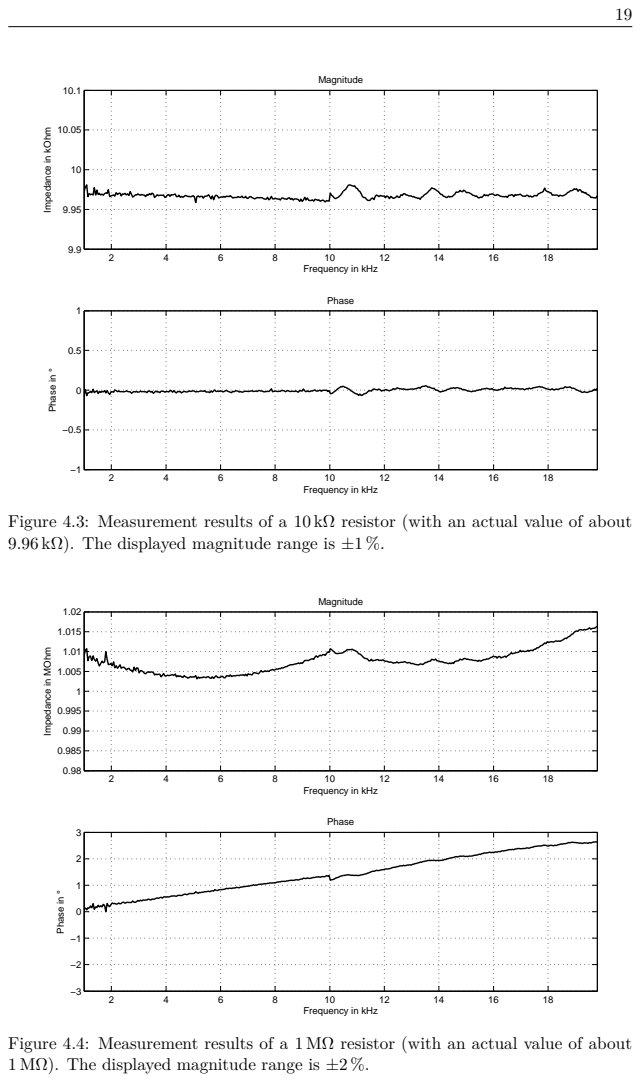
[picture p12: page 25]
Magnitude; Phase in °; Phase

Impedance in kOhm

Frequency in kHz

Figure 4.3: Measurement results of a 10 kΩ resistor (with an actual value of about
9.96 kΩ). The displayed magnitude range is ±1 %.

Impedance in MOhm

Figure 4.4: Measurement results of a 1 MΩ resistor (with an actual value of about
1 MΩ). The displayed magnitude range is ±2 %.

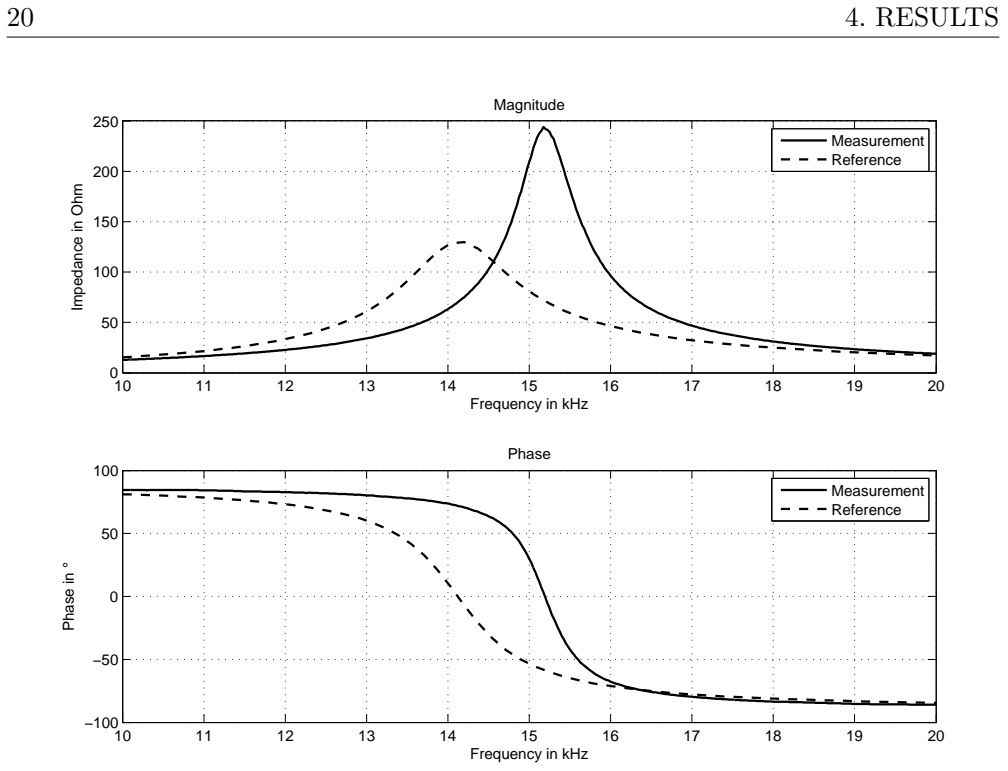
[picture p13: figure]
4. RESULTS; Frequency in kHz; Impedance in Ohm; Magnitude; Measurement Reference; Phase in °; Phase

Figure 4.5: Measurement results of a high-Q LC resonant circuit (1 µF k 100 µH). The solid line represents the measured value, the dashed line the actual impedance obtained from an Agilent 4294A impedance analyzer.

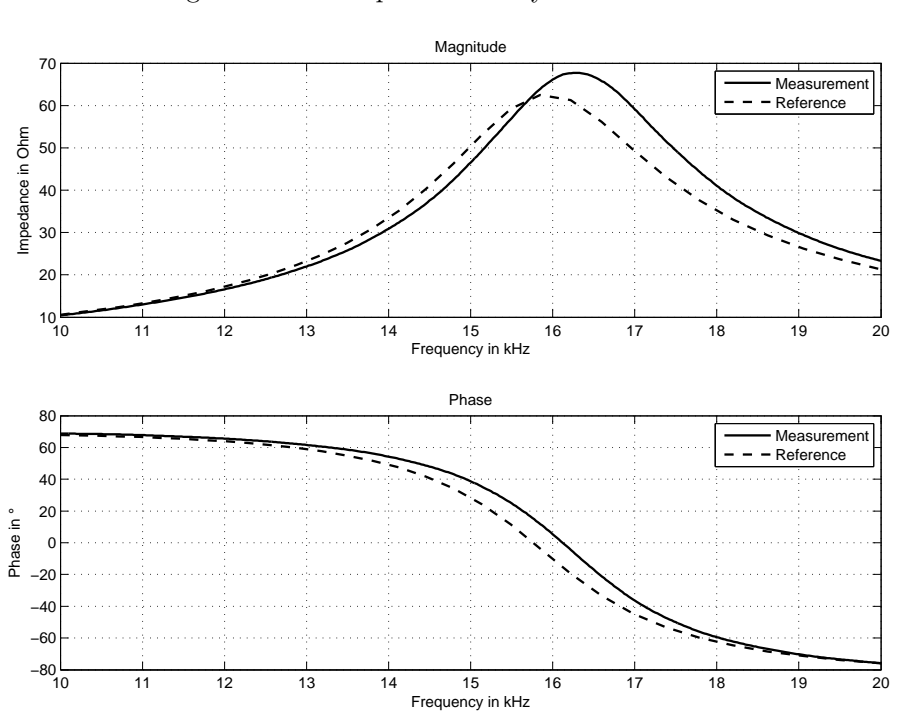
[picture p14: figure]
Frequency in kHz; Impedance in Ohm; Magnitude; Measurement Reference; Phase in °; Phase; Measurement; Reference

Figure 4.6: Measurement results of a low-Q LC resonant circuit (1 µF k 100 µH). The solid line represents the measured value, the dashed line the actual impedance obtained from an Agilent 4294A impedance analyzer.

21

# 5 User’s Manual

This manual will describe the impedance spectrometer in detail and give step by step instructions for using it.

## 5.1 Overview

An overview of the device connections can be seen in Figure 5.1. Connector footprints for unimplemented features are not labeled, the push buttons on the board are the same as those on the STM32F4 Discovery board.

The USB programming connector 1 is used to program and debug the device, but it can also be used to power the device from a standard phone charger or similar supply with a Mini-B USB plug. The device USB connector 2 is used to connect the device to a PC and control it. The DC jack 5 is a standard 2.5 mm jack (center positive) and can be used to power the device with a 5 V DC supply.

When using the device with an external power supply, or powered from the programming connector 1, the VBUS jumper 12 may be disconnected to prevent the board from drawing power from the device connector 2.

The jumpers 10 and 11 can be used to measure the current consumption of the microcontroller and all the other parts, respectively (note that there are two jumpers

for IDD, one on the STM32F4 Discovery board and one on the board, and care should be taken to use only one).

There are four status LEDs 3, three of which are used at this time:

- blue (bottom) will blink when the device is powered on, indicating that the

firmware has not locked up,

- green (left) will light up while a measurement is in progress, allowing the user

to see when it has finished,

- red (right) will be turned on in case of an error in the firmware, which means

the device should be reset using the reset button 4 and the steps leading up to the error should be documented, allowing the programmer to fix it.

22 | 5. USER’S MANUAL

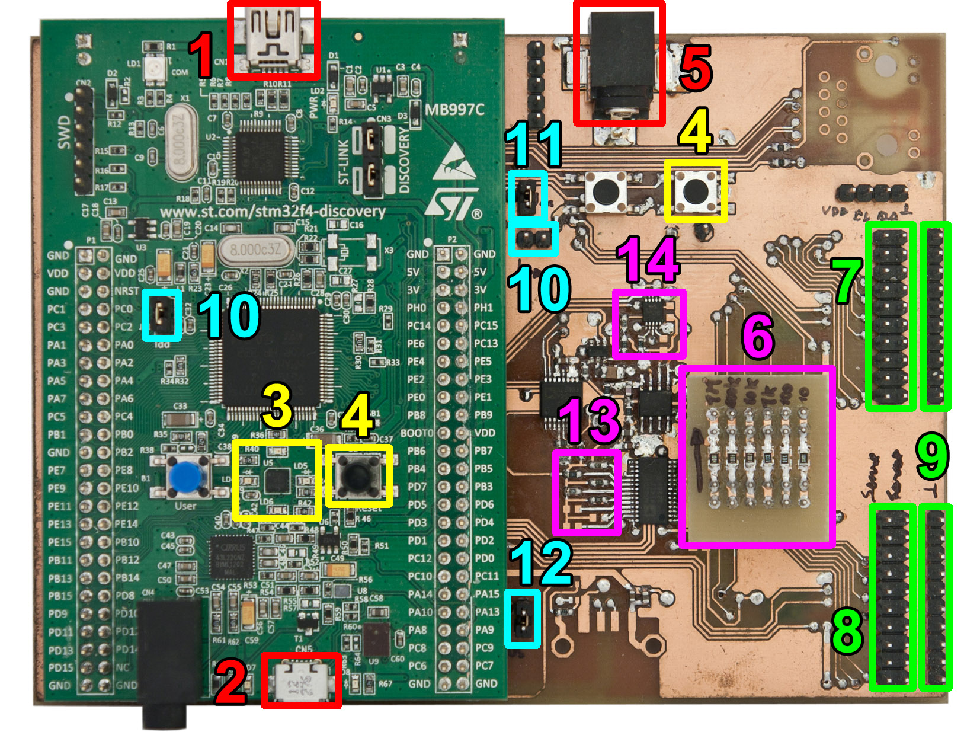
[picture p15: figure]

Figure 5.1: Interface on the assembled impedance spectrometer: 1 USB programming and power connector – 2 device USB connector – 3 status LEDs – 4 reset button – 5 DC power jack – 6 board with calibration resistors – 7 measurement output connections, sense (left) and force (right) – 8 measurement input connections (same as output) – 9 ground connections – 10 IDD measurement jumper –

### 11 ICC measurement jumper – 12 VBUS jumper – 13 feedback resistors – 14 atten-

uation resistors

### 5.1.1 First Steps

Before powering up the device for the first time, the following things should be checked:

- the STM32F4 discovery board is properly connected,
- a board with calibration resistors is connected to the calibration pins 6,
- the necessary feedback and attenuation resistors 13 and 14 are soldered on,
- the current measurement jumpers 10 and 11 are connected (or a current meter of course),
- the VBUS jumper 12 is connected when no external power supply is used.

After connecting the device to a PC, any application that can access a serial port can be used to communicate with it. Settings such as baud rate or parity do not matter.

5.2. MAKING MEASUREMENTS | 23

When not using the MATLAB functions (see section 3.2), the device is configured

via a simple virtual console interface using human readable commands. By typing help, a list of possible commands and their explanations can be displayed.

The following steps assume the device is fitted with an EEPROM for configuration storage. The first thing to do after assembling the device is to configure the fitted calibration and feedback resistors, as well as possible attenuations and the coupling capacitor time constant using the setup command:

- enter possible output voltage attenuations in the order they are selected with

the attenuation multiplexer: setup attenuation <values>...

- enter feedback resistor values in the order they are connected to the feedback

multiplexer in ohms: setup feedback <values>...

- enter calibration resistor values in the order they are soldered on the little

resistor board (right to left): setup calibration <values>...

- enter the coupling capacitor time constant in ms (calculated by Ccoupl · 1.1 kΩ):

setup coupl <milliseconds>

Typing help setup shows other options for the setup command; however, none of them are currently used since the respective peripherals are not yet implemented.

By typing board info, general information for the whole board is displayed, which includes the configured resistors and attenuation values.

## 5.2 Making Measurements

After the first steps have been completed, measurements can be performed.

First, the unknown impedance(s) need to be connected to the output and input

connectors 7 and 8. When a four-wire connection is not used, the two output and input pins, respectively, need to be connected nonetheless for proper operation.

### 5.2.1 Sweep Configuration

Then, the sweep parameters need to be configured. This is done using the board set command with the following parameters (only those that should be changed need to be sent):

- --start=FREQ and --stop=FREQ set the start and stop frequency of the sweep

in Hz. Note that when setting start and stop frequency in a single command, an error can occur when the new start frequency is equal to or higher than the previous stop frequency. In this case you need to change the order in which start and stop options appear on the command line.

24 | 5. USER’S MANUAL
- --steps=NUM sets the number of frequency steps in a sweep, that is the number

of times the frequency is incremented.

- --settl=NUM sets the number of settling cycles (see subsection 2.1.1). The

valid range is 0–511 and can be extended 2 or 4 times by specifying a multiplier like x2. For example, valid values would be 20 or 40x2, but not 512 (use 256x2 instead).

- --voltage=RANGE sets the output voltage range in mV. The possible ranges

are determined by the configured attenuation values, they are one of the AD5933 output voltages (200 mV, 400 mV, 1 V or 2 V) divided by one of the

attenuation values. For example, if attenuation values of 1 and 100 were configured, the possible voltage ranges would be 2000, 1000, 400, 200, 20, 10, 4 and 2.

- --gain=(on|off) sets whether the input gain stage (PGA) is enabled. When

enabled, the input signal is amplified by a factor of 5 prior to sampling.

- --feedback=OHMS sets the used feedback resistor, this needs to be one of the

configured values.

The current value for any parameter can be displayed with the board get command, which accepts one of the parameters and displays its value (for example board get start would display the start frequency in Hz). A quick overview of the

current values can be displayed by typing board get all, which displays all sweep parameters in a format suitable for parsing by PC software.

When selecting range settings, the following procedure should be used:

- Set the output voltage low enough so the output current does not exceed 10 mA

with the lowest impedance expected.

- Set the current feedback resistor to a value low enough so the input voltage

stays below 3V for the highest output current expected.

- If necessary, the PGA can be enabled to further amplify the input voltage

when high impedances are to be measured. For accurate results, the input signal should be close to 3V for the lowest impedance expected.

### 5.2.2 Calibration

Before measurements can be made the system has to be calibrated with a known impedance (see subsection 2.1.1 on why this is necessary). After the range settings (start and stop frequency, output voltage, feedback resistor, or PGA gain)

are changed, the board calibrate command is used to do that. The calibration

5.2. MAKING MEASUREMENTS | 25

impedance, specified as the only parameter to the command, should be in the same range as the impedance to be measured for accurate results.

A recalibration is also necessary when the ambient temperature changes significantly.

Normally, calibration resistors are connected to the device with the small PCB 6 mounted on the calibration connectors. However, those connectors are just measurement connectors like 7 and 8, so calibration resistors can also be connected without a dedicated calibration resistor board. Note that resistors should always be used for calibration, because the calibration impedance must not introduce a phase shift of its own.

### 5.2.3 Starting a Sweep

Once the sweep parameters are set and a calibration has been performed, a sweep can be started. Typing board start with the desired port number as the only parameter will initiate a sweep, indicated by the green LED 3 lighting up. The port number determines which pair of pins will be used, with the topmost pins having the number 0 and the bottom pins the number 9. The valid range can also be displayed with the board info command.

While a sweep is running, the status can be displayed by typing board status. This will print the number of points already measured, and whether the sweep is still running or has finished.

A running measurement can be stopped by typing board stop, which also resets the AD5933 and disconnects the output and input pins. To disconnect the outputs

when no measurement is running board standby can be used.

### 5.2.4 Reading Results

After a sweep is finished, the measurement results can be read with the board read command. The format in which measurement data is transferred can either be set permanently with the board set --format=FMT command, or specified to the board read command for a single transfer.

The format specification is a set of flags, represented by uppercase letters. There are two modes for data transfer, ASCII and binary. All possible flags can be found

in Table 5.1.

When using binary format, at least one of the P and C flags has to be specified. The H flag causes the number of bytes to follow to be transferred at the start of the transmission as an unsigned 32 bit integer. The frequency is also transferred as

26 | 5. USER’S MANUAL

an unsigned 32 bit integer, the impedance values (magnitude and angle, or real and imaginary parts) as single precision 32 bit floating point values.

When using ASCII format, at least one of the P and C flags, one of the F and X flags, as well as one of three separator flags have to be specified. The data is transferred in human readable form, one line per record, with values separated by the specified separator character. After the last record, two line breaks are sent to signal the end of the transmission. The H flag causes a header line to be transferred before the first record.

Table 5.1: Possible format flags for transferring measurement data.

Flag | Function
A | Selects ASCII transfer format
B | Selects binary transfer format
P | Selects polar number format (magnitude in ohms and angle
| in radians)
C | Selects Cartesian number format (real and imaginary parts
| in ohms)
H | When present, a header is printed for ASCII format, or the
| byte count is transferred for binary format
F | ASCII only: impedance values are printed as formatted
| floating point values, the frequency as an unsigned integer
X | ASCII only: frequency and impedance values are printed as
| hexadecimal values
S | ASCII only: Selects a space character as the separator
T | ASCII only: Selects a tab character as the separator
D | ASCII only: Selects a comma character as the separator
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

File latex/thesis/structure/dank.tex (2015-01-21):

\chapter{Acknowledgment}

First of all, I want to thank my supervisor DI Stefan Clara for his support and for the opportunity to work on a, more
or less, real world project, where I could combine the two things I like most about electronics: circuit design and
programming.

A big thank you also goes out to my father Klaus, who continues to enable my studies and my life in Linz, despite
him having to support four kids.
I know I am not always easy to deal with and I am very grateful for your support and love.

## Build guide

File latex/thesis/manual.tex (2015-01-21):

\chapter{User's Manual} \label{sec:manual}

This manual will describe the impedance spectrometer in detail and give step by step instructions for using it.

\section{Overview}

An overview of the device connections can be seen in Figure \ref{fig:device_connections}. Connector footprints for
unimplemented features are not labeled, the push buttons on the board are the same as those on the
STM32F4 Discovery board.

\begin{figure}[htb]
  \centering
    
  \caption[Interface on the assembled impedance spectrometer]{
    Interface on the assembled impedance spectrometer:
    \begin{enumerate*}[label=\textbf{\arabic*}, itemjoin={{ -- }}]
      \item \label{itm:usb_prog}  USB programming and power connector
      \item \label{itm:usb_dev}   device USB connector
      \item \label{itm:leds}      status LEDs
      \item \label{itm:btn_rst}   reset button
      \item \label{itm:dc_jack}   DC power jack
      \item \label{itm:r_cal}     board with calibration resistors
      \item \label{itm:meas_out}  measurement output connections, sense (left) and force (right)
      \item \label{itm:meas_in}   measurement input connections (same as output)
      \item \label{itm:meas_gnd}  ground connections
      \item \label{itm:jump_idd}  $ I_\text{DD} $ measurement jumper
      \item \label{itm:jump_icc}  $ I_\text{CC} $ measurement jumper
      \item \label{itm:jump_vbus} $ V_\text{BUS} $ jumper
      \item \label{itm:r_fb}      feedback resistors
      \item \label{itm:r_att}     attenuation resistors
    \end{enumerate*} }
  \label{fig:device_connections}
\end{figure}

The USB programming connector \ref{itm:usb_prog} is used to program and debug the device, but it can also be used to
power the device from a standard phone charger or similar supply with a Mini-B USB plug.
The device USB connector \ref{itm:usb_dev} is used to connect the device to a PC and control it.
The DC jack \ref{itm:dc_jack} is a standard \unit{2.5}{\milli\meter} jack (center positive) and can be used to
power the device with a \unit{5}{\volt} DC supply.

When using the device with an external power supply, or powered from the programming connector \ref{itm:usb_prog},
the $ V_\text{BUS} $ jumper \ref{itm:jump_vbus} may be disconnected to prevent the board from drawing power from the
device connector \ref{itm:usb_dev}.

The jumpers \ref{itm:jump_idd} and \ref{itm:jump_icc} can be used to measure the current consumption of the
microcontroller and all the other parts, respectively (note that there are two jumpers for $ I_\text{DD} $,
one on the STM32F4 Discovery board and one on the board, and care should be taken to use only one).

There are four status LEDs \ref{itm:leds}, three of which are used at this time:
\begin{itemize}
	\item \textbf{\color{blue} blue} (bottom) will blink when the device is powered on, indicating that the firmware
    has not locked up,
  \item \textbf{\color{OliveGreen} green} (left) will light up while a measurement is in progress, allowing the user
    to see when it has finished,
  \item \textbf{\color{red} red} (right) will be turned on in case of an error in the firmware, which means the device
    should be reset using the reset button \ref{itm:btn_rst} and the steps leading up to the error should be
    documented, allowing the programmer to fix it.
\end{itemize}

\subsection{First Steps}

Before powering up the device for the first time, the following things should be checked:
\begin{itemize}
	\item the STM32F4 discovery board is properly connected,
  \item a board with calibration resistors is connected to the calibration pins \ref{itm:r_cal},
  \item the necessary feedback and attenuation resistors \ref{itm:r_fb} and \ref{itm:r_att} are soldered on,
  \item the current measurement jumpers \ref{itm:jump_idd} and \ref{itm:jump_icc} are connected
    (or a current meter of course),
  \item the $ V_\text{BUS} $ jumper \ref{itm:jump_vbus} is connected when no external power supply is used.
\end{itemize}

After connecting the device to a PC, any application that can access a serial port can be used to communicate with it.
Settings such as baud rate or parity do not matter.
When not using the MATLAB functions (see \autoref{sec:matlab}), the device is configured via a simple virtual console
interface using human readable commands. By typing \command{help}, a list of possible commands and their
explanations can be displayed.

The following steps assume the device is fitted with an EEPROM for configuration storage.
The first thing to do after assembling the device is to configure the fitted calibration and feedback resistors, as well
as possible attenuations and the coupling capacitor time constant using the \command{setup} command:
\begin{itemize}
	\item enter possible output voltage attenuations in the order they are selected with the attenuation multiplexer:
    \command{setup attenuation <values>...}
  \item enter feedback resistor values in the order they are connected to the feedback multiplexer in ohms:
    \command{setup feedback <values>...}
  \item enter calibration resistor values in the order they are soldered on the little resistor board (right to left):
    \command{setup calibration <values>...}
  \item enter the coupling capacitor time constant in ms (calculated by $ C_\text{coupl} \cdot \unit{1.1}{\kilo\ohm} $):
    \command{setup coupl <milliseconds>}
\end{itemize}
Typing \command{help setup} shows other options for the \command{setup} command; however, none of them are currently
used since the respective peripherals are not yet implemented.

By typing \command{board info}, general information for the whole board is displayed, which includes the configured
resistors and attenuation values.

\section{Making Measurements}

After the first steps have been completed, measurements can be performed.

First, the unknown impedance(s) need to be connected to the output and input connectors \ref{itm:meas_out} and
\ref{itm:meas_in}. When a four-wire connection is not used, the two output and input pins, respectively, need to be
connected nonetheless for proper operation.

\subsection{Sweep Configuration}

Then, the sweep parameters need to be configured. This is done using the \command{board set} command with the following
parameters (only those that should be changed need to be sent):
\begin{itemize}
	\item \command{--start=FREQ} and \command{--stop=FREQ} set the start and stop frequency of the sweep in \hertz.
    Note that when setting start and stop frequency in a single command, an error can occur when the new start
    frequency is equal to or higher than the previous stop frequency. In this case you need to change the order in
    which start and stop options appear on the command line.
  \item \command{--steps=NUM} sets the number of frequency steps in a sweep, that is the number of times the frequency
    is incremented.
  \item \command{--settl=NUM} sets the number of settling cycles (see \autoref{sec:ad5933_proc}). The valid range is
    0--511 and can be extended 2 or 4 times by specifying a multiplier like \command{x2}. For example, valid values
    would be \command{20} or \command{40x2}, but not \command{512} (use \command{256x2} instead).
  \item \command{--voltage=RANGE} sets the output voltage range in \milli\volt. The possible ranges are determined by
    the configured attenuation values, they are one of the AD5933 output voltages (\unit{200}{\milli\volt},
    \unit{400}{\milli\volt}, \unit{1}{\volt} or \unit{2}{\volt}) divided by one of the attenuation values. For example,
    if attenuation values of 1 and 100 were configured, the possible voltage ranges would be 2000, 1000, 400, 200, 20,
    10, 4 and 2.
  \item \command{--gain=(on|off)} sets whether the input gain stage (PGA) is enabled. When enabled, the input signal is
    amplified by a factor of 5 prior to sampling.
  \item \command{--feedback=OHMS} sets the used feedback resistor, this needs to be one of the configured values.
\end{itemize}
The current value for any parameter can be displayed with the \command{board get} command, which accepts one of the
parameters and displays its value (for example \command{board get start} would display the start frequency in \hertz).
A quick overview of the current values can be displayed by typing \command{board get all}, which displays all sweep
parameters in a format suitable for parsing by PC software.

When selecting range settings, the following procedure should be used:
\begin{itemize}
	\item Set the output voltage low enough so the output current does not exceed \unit{10}{\milli\ampere} with the
    lowest impedance expected.
  \item Set the current feedback resistor to a value low enough so the input voltage stays below 3V for the highest
    output current expected.
  \item If necessary, the PGA can be enabled to further amplify the input voltage when high impedances are to be
    measured. For accurate results, the input signal should be close to 3V for the lowest impedance expected.
\end{itemize}

\subsection{Calibration}

Before measurements can be made the system has to be calibrated with a known impedance (see \autoref{sec:ad5933_proc}
on why this is necessary). After the range settings (start and stop frequency, output voltage, feedback resistor, or
PGA gain) are changed, the \command{board calibrate} command is used to do that. The calibration impedance, specified
as the only parameter to the command, should be in the same range as the impedance to be measured for accurate results.

A recalibration is also necessary when the ambient temperature changes significantly.

Normally, calibration resistors are connected to the device with the small PCB \ref{itm:r_cal} mounted on the
calibration connectors. However, those connectors are just measurement connectors like \ref{itm:meas_out} and
\ref{itm:meas_in}, so calibration resistors can also be connected without a dedicated calibration resistor board.
\emph{Note that resistors should always be used for calibration, because the calibration impedance must not introduce
  a phase shift of its own.}

\subsection{Starting a Sweep}

Once the sweep parameters are set and a calibration has been performed, a sweep can be started.
Typing \command{board start} with the desired port number as the only parameter will initiate a sweep, indicated by
the green LED \ref{itm:leds} lighting up. The port number determines which pair of pins will be used, with the topmost
pins having the number 0 and the bottom pins the number 9. The valid range can also be displayed with the
\command{board info} command.

While a sweep is running, the status can be displayed by typing \command{board status}. This will print the number of
points already measured, and whether the sweep is still running or has finished.

A running measurement can be stopped by typing \command{board stop}, which also resets the AD5933 and disconnects the
output and input pins. To disconnect the outputs when no measurement is running \command{board standby} can be used.

\subsection{Reading Results}

After a sweep is finished, the measurement results can be read with the \command{board read} command.
The format in which measurement data is transferred can either be set permanently with the
\command{board set --format=FMT} command, or specified to the \command{board read} command for a single transfer.

The format specification is a set of flags, represented by uppercase letters. There are two modes for data transfer,
ASCII and binary. All possible flags can be found in \autoref{tab:format_flags}.

When using binary format, at least one of the \texttt{P} and \texttt{C} flags has to be specified. The \texttt{H} flag
causes the number of bytes to follow to be transferred at the start of the transmission as an unsigned \unit{32}{bit}
integer. The frequency is also transferred as an unsigned \unit{32}{bit} integer, the impedance values (magnitude and
angle, or real and imaginary parts) as single precision \unit{32}{bit} floating point values.

When using ASCII format, at least one of the \texttt{P} and \texttt{C} flags, one of the \texttt{F} and \texttt{X}
flags, as well as one of three separator flags have to be specified. The data is transferred in human readable form,
one line per record, with values separated by the specified separator character. After the last record, two line breaks
are sent to signal the end of the transmission. The \texttt{H} flag causes a header line to be transferred before the
first record.

\begin{table}[htpb]
  \caption{Possible format flags for transferring measurement data.}
  \centering
  \begin{tabular}{>{\ttfamily\bgroup}l<{\egroup} !{\color{MidnightBlue}\vline} p{10cm}}
    \arrayrulecolor{MidnightBlue}
    Flag  & Function \\ \hline \hline
    A     & Selects ASCII transfer format \\
    B     & Selects binary transfer format \\ \hline
    P     & Selects polar number format (magnitude in ohms and angle in radians) \\
    C     & Selects Cartesian number format (real and imaginary parts in ohms) \\ \hline
    H     & When present, a header is printed for ASCII format, or the byte count is transferred for binary format \\ \hline
    F     & ASCII only: impedance values are printed as formatted floating point values, the frequency as an unsigned integer \\
    X     & ASCII only: frequency and impedance values are printed as hexadecimal values \\ \hline
    S     & ASCII only: Selects a space character as the separator \\
    T     & ASCII only: Selects a tab character as the separator \\
    D     & ASCII only: Selects a comma character as the separator
  \end{tabular}
  \label{tab:format_flags}
\end{table}

\section{Additional Commands}

There are some additional commands and options which are not necessarily useful for normal operation; those are
explained in this section.

The \command{board temp} command can be used to make a temperature measurement using the AD5933's internal temperature
sensor. The value is reasonably accurate to \unit{\pm 2}{\celsius}, but usually higher than the ambient temperature due
to the power dissipation of the AD5933.

The \command{board set} command accepts the \command{--avg=NUM} parameter, which sets the number of averages for each
frequency point and can be in the range from 1 to 65535.
It also accepts the \command{--autorange=(on|off)} parameter, however, this currently has no effect since autoranging is
not yet implemented.

The \command{board measure} command accepts a port and frequency and can be used to measure the impedance at a port at
one specific frequency. The result is printed as a polar value in ASCII format when the measurement is finished.

The \command{board read} command accepts the additional options \command{--raw} and \command{--gain}, one of which may
be specified at a time. Using these options, the raw measurement data (as received from the AD5933) or the gain factor,
respectively, can be transferred. The raw measurement data is always transferred in Cartesian coordinate format, all
other format flags have the usual effect. The gain factor is always transferred in the same format, as a list of
floating point values.

\section{Using the MATLAB Interface}

To use the device with MATLAB (e.g.\ for automated measurements) a set of functions is provided that utilize the
virtual console interface of the device. \autoref{lst:test_measure} shows a demo script that performs a measurement and
plots the results.

All functions take a MATLAB serial port object as their first parameter, which needs to be \texttt{fopen}ed beforehand.
The \texttt{Timeout} property on the serial port object needs to be set quite high when low frequencies should be
measured (\unit{120}{\second} should be high enough), the \texttt{Terminator} property should be set to
\matlab{'CR/LF'} or \matlab{\{'CR/LF','LF'\}} for proper operation.

The basic procedure is not very complicated:
\begin{itemize}
	\item After creating a structure with sweep parameters (see lines 6--14) they are sent to the device using the
    \matlab{impy_setsweep} function. A parameter structure can also be obtained with the \matlab{impy_getall} function,
    which reads the current sweep parameters from the device and returns one.
  \item Then a calibration is performed using the \matlab{impy_calibrate} function, which takes the calibration resistor
    value as the second parameter. Note that this function does not return until the calibration is complete, which
    can take some time when low frequencies are to be measured. This is the reason a large timeout value needs to be
    set on the serial port object.
  \item The measurement can then be started with the \matlab{impy_start} function, which takes the port as the second
    parameter. Note that this function returns immediately after starting a measurement.
  \item After the measurement has been started, the \matlab{impy_poll} function is used to check when it has finished.
    This function returns whether the measurement has finished or not and, in case it has, the number of points that
    have been measured.
  \item The last step is to read the measurement data using the \matlab{impy_read} function, which accepts and optional
    second parameter for the desired format, which can be \emph{polar}, \emph{cartesian} or \emph{raw}. This function
    returns a frequency vector and, depending on the format, either an array with magnitude and angle, a vector with
    complex impedance values, or an array with raw real and imaginary values.
\end{itemize}

All functions throw errors when the serial connection is interrupted or the board responds with some unrecognized
output. This can happen when the firmware is changed and the MATLAB functions are not updated accordingly.

There is also a function to display the output of the \command{help} command, \matlab{impy_help}, which takes an
optional help topic as the second parameter.

\lstinputlisting[columns=flexible,
  float=htpb,
  caption={MATLAB demo script using the interface functions to control the device.},
  label=lst:test_measure]
  {code/test_measure.m}

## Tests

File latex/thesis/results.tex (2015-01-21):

\chapter{Results} \label{sec:results}

The performance of the device was analyzed by measuring some resistors and other mixed networks.

With small resistors in the range of a few \unit{10}{\ohm} to \unit{10}{\kilo\ohm}, the accuracy is better than
\unit{1}{\%}.
\autoref{fig:meas_49r9} shows a measurement of a \unit{49.9}{\ohm} resistor,
\autoref{fig:meas_5k6} shows the results with a \unit{5.6}{\kilo\ohm} resistor
and \autoref{fig:meas_10k} the results with a \unit{10}{\kilo\ohm} resistor.
Every profile is well within the \unit{\pm 1}{\%} range, the impedance angle is close to 0, as would be expected from
an ohmic resistor.

For resistors of larger magnitude, the accuracy is not as good; a measurement of a \unit{1}{\mega\ohm} resistor can be
seen in \autoref{fig:meas_1M}. There are non-linear terms in the system gain that are not compensated by the two-point
calibration, which result in the nonlinear impedance profile. The measured angle shows a linear trend, which should
be compensated by the two-point calibration but is not.
Also note the change in slope and noise at \unit{10}{\kilo\hertz}, where the clock source is switched from the external
source below \unit{10}{\kilo\hertz} to the internal one above.

When sweeping over larger frequency ranges, the accuracy is not as good, especially in the range near or above
\unit{100}{\kilo\hertz}.
In general, it is advisable to use a frequency range as narrow as possible, since the two-point calibration can only
account for constant and linear terms in the system gain. Nonlinearities however only manifest when a large frequency
range is swept all at once.

For small mixed impedance networks, however, the results are quite bad. Because of  an instability in the external AFE,
the measurement results cannot be used at all. \autoref{fig:meas_S22} shows a measurement of a high-Q LC resonant
circuit, as can be seen the impedance value as well as the resonant frequency of the circuit are way off.
A similar LC circuit with a lower Q-factor shows better results (compare \autoref{fig:meas_LCP}), the accuracy is not
good enough nonetheless.

A goal for further work on the device is to replace the current topology of the external analog front end
(inverting amplifier configured as an attenuator on the output, current to voltage conversion on the input)
by a different one. A possible approach is to use a current source on the output and directly measure the voltage
across the impedance on the input.

\begin{figure}[htpb]
  \centering
    
  \caption{Measurement results of a \unit{49.9}{\ohm} resistor (with an actual value of about \unit{50}{\ohm}).
    The displayed magnitude range is \unit{\pm 1}{\%}.}
  \label{fig:meas_49r9}
\end{figure}

\begin{figure}[htpb]
  \centering
    
  \caption{Measurement results of a \unit{5.6}{\kilo\ohm} resistor (with an actual value of about \unit{5.58}{\kilo\ohm}).
    The displayed magnitude range is \unit{\pm 1}{\%}.}
  \label{fig:meas_5k6}
\end{figure}

\begin{figure}[htpb]
  \centering
    
  \caption{Measurement results of a \unit{10}{\kilo\ohm} resistor (with an actual value of about \unit{9.96}{\kilo\ohm}).
    The displayed magnitude range is \unit{\pm 1}{\%}.}
  \label{fig:meas_10k}
\end{figure}

\begin{figure}[htpb]
  \centering
    
  \caption{Measurement results of a \unit{1}{\mega\ohm} resistor (with an actual value of about \unit{1}{\mega\ohm}).
    The displayed magnitude range is \unit{\pm 2}{\%}.}
  \label{fig:meas_1M}
\end{figure}

\begin{figure}[htpb]
  \centering
    
  \caption{Measurement results of a high-Q LC resonant circuit ($ \unit{1}{\micro\farad} \,\|\, \unit{100}{\micro\henry} $).
    The solid line represents the measured value, the dashed line the actual impedance obtained from an Agilent 4294A
    impedance analyzer. }
  \label{fig:meas_S22}
\end{figure}

\begin{figure}[htpb]
  \centering
    
  \caption{Measurement results of a low-Q LC resonant circuit ($ \unit{1}{\micro\farad} \,\|\, \unit{100}{\micro\henry} $).
    The solid line represents the measured value, the dashed line the actual impedance obtained from an Agilent 4294A
    impedance analyzer. }
  \label{fig:meas_LCP}
\end{figure}

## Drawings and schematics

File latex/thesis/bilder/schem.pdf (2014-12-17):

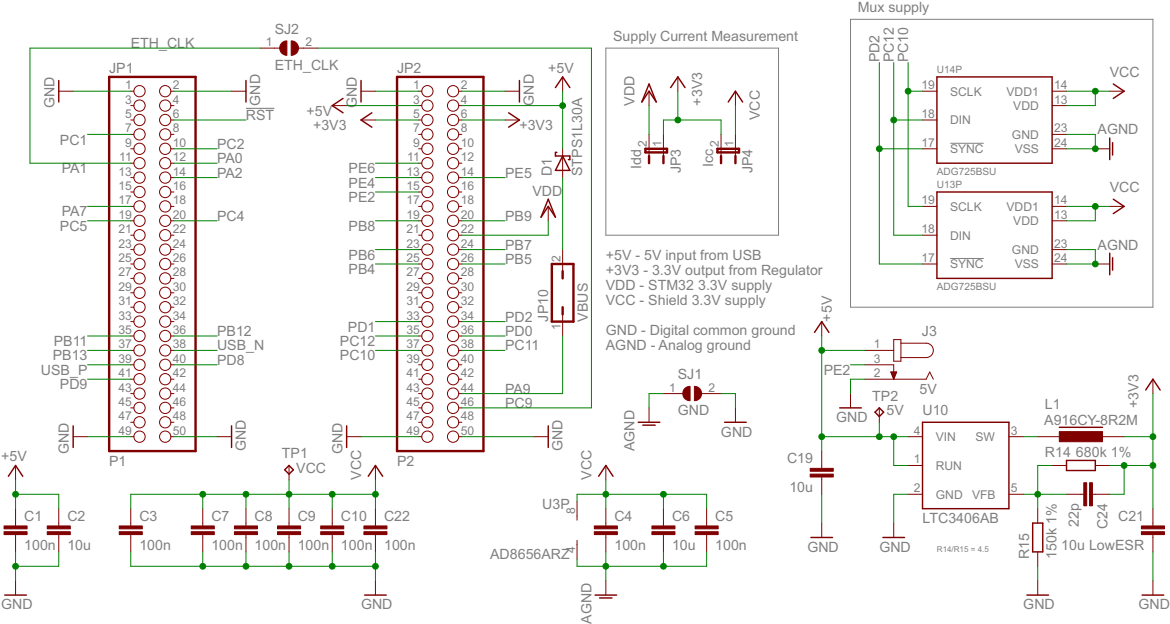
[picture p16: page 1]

+5V - 5V input from USB
+3V3 - 3.3V output from Regulator VDD - STM32 3.3V supply

GND - Digital common ground
AGND - Analog ground

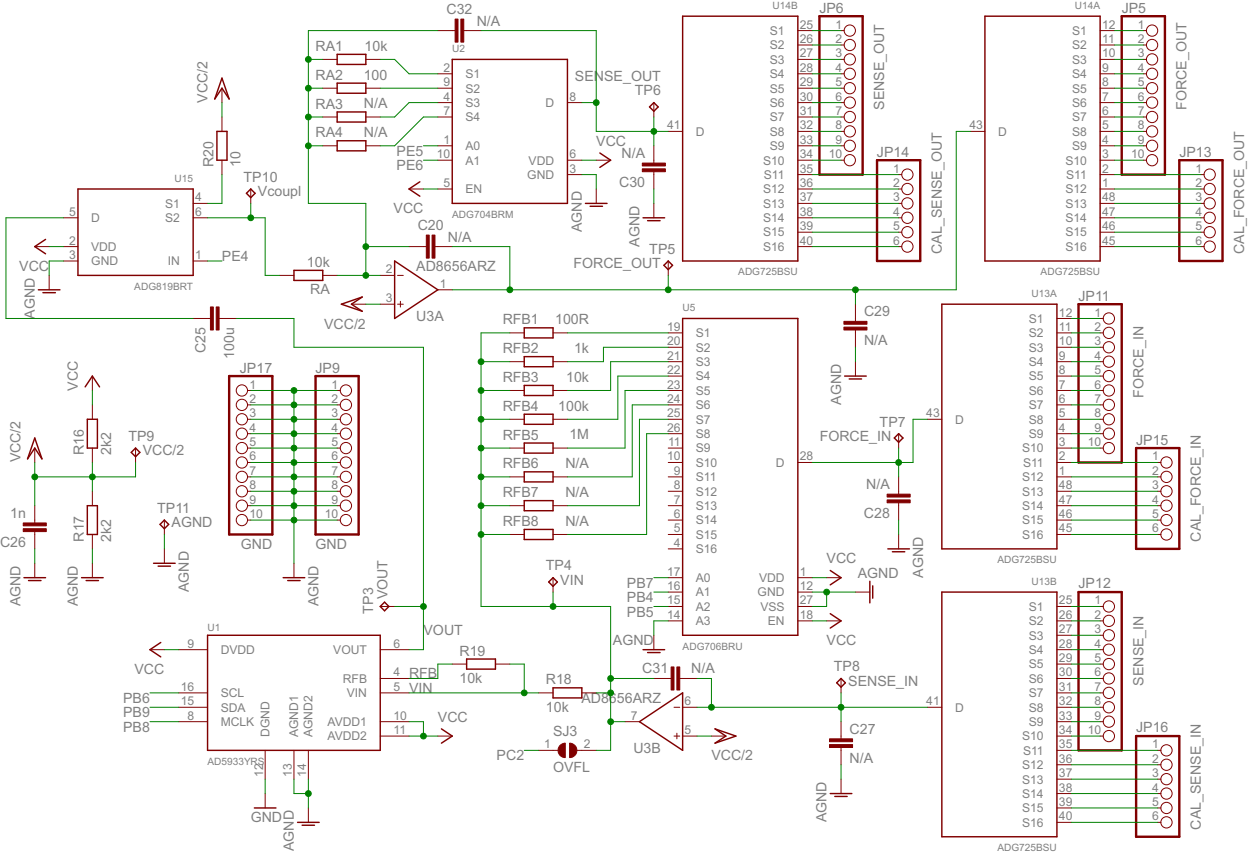
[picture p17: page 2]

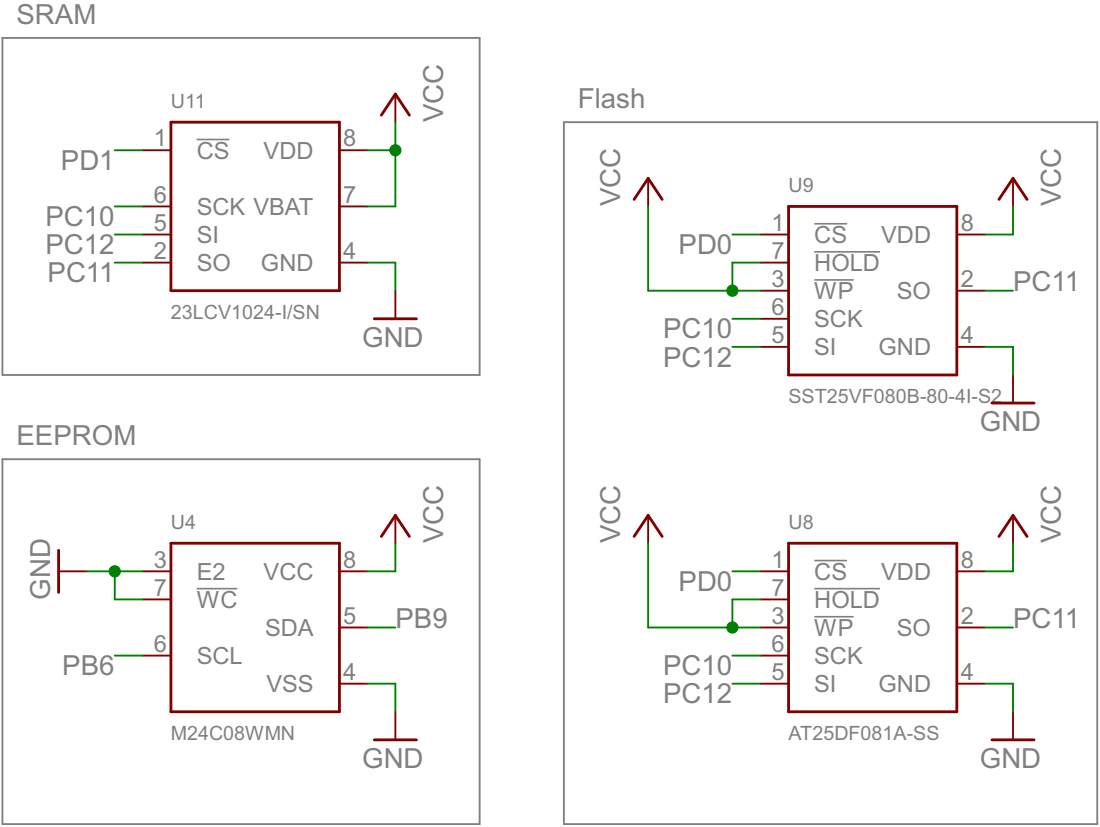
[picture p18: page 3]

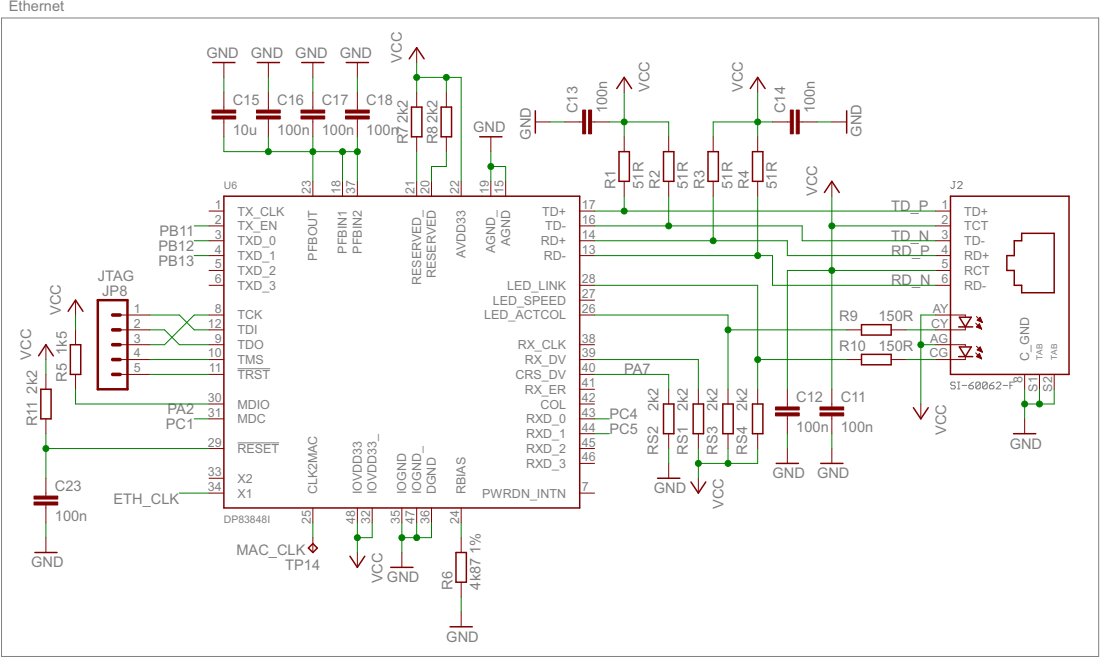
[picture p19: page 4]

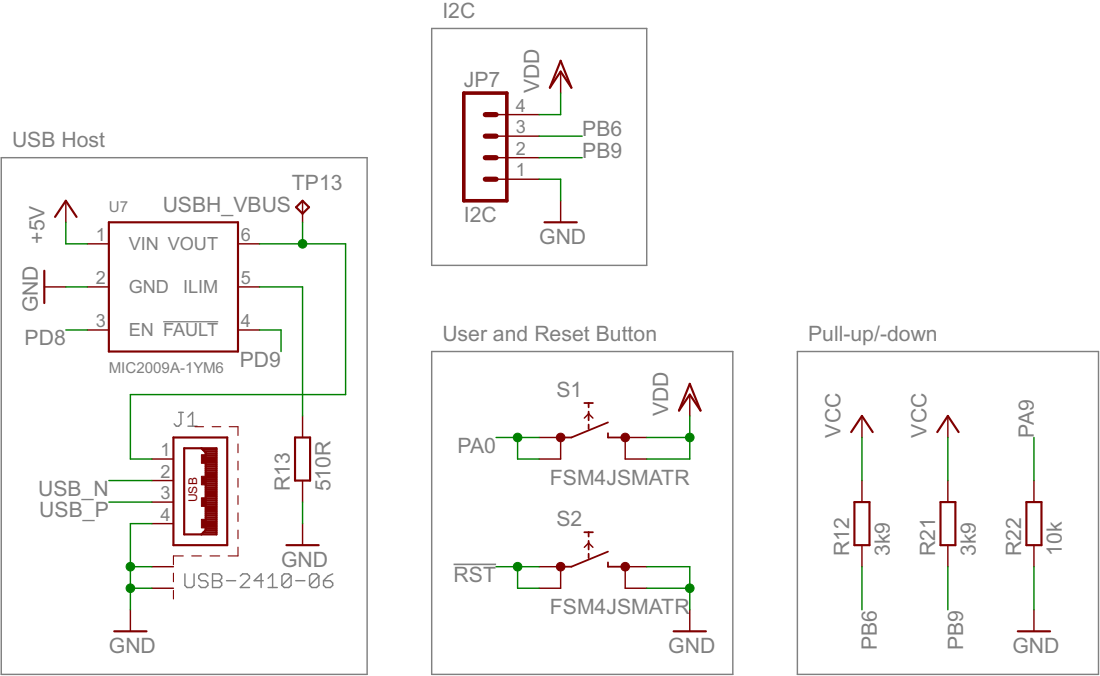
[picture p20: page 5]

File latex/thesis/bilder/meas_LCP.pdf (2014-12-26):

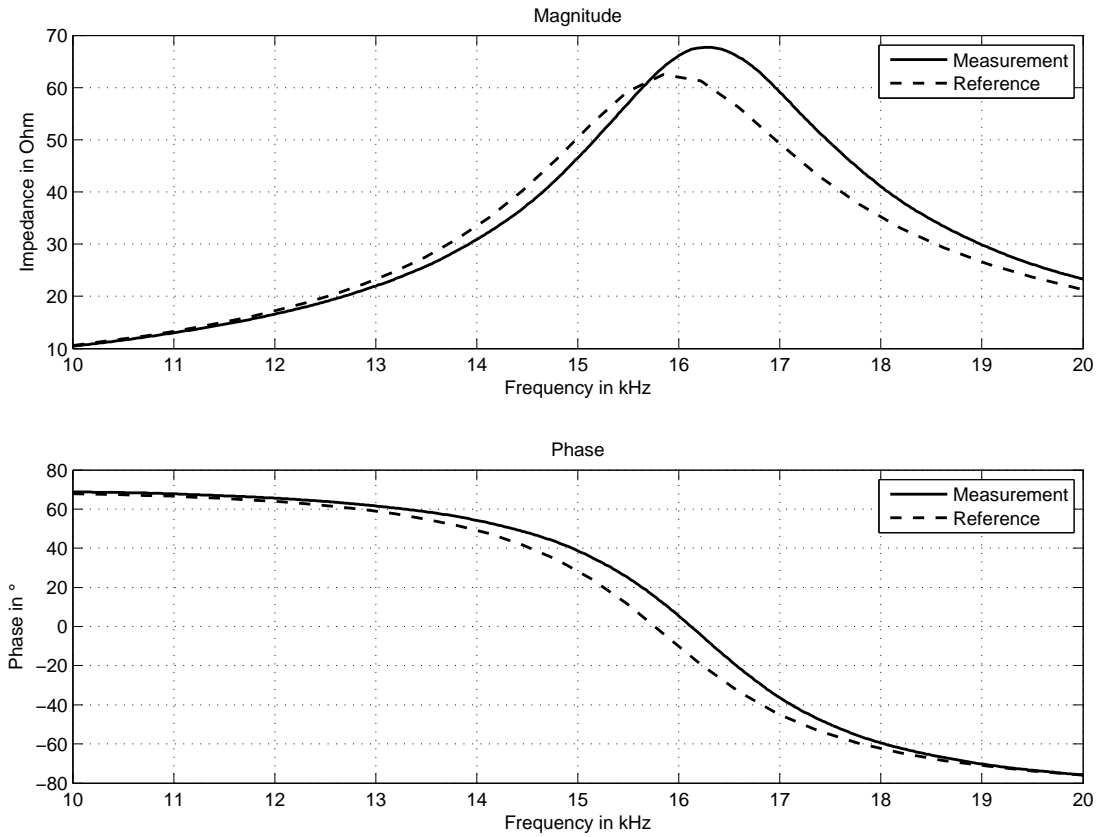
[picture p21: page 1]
Magnitude; Measurement Reference; Phase in °; Phase

Impedance in Ohm

Frequency in kHz

Measurement
Reference

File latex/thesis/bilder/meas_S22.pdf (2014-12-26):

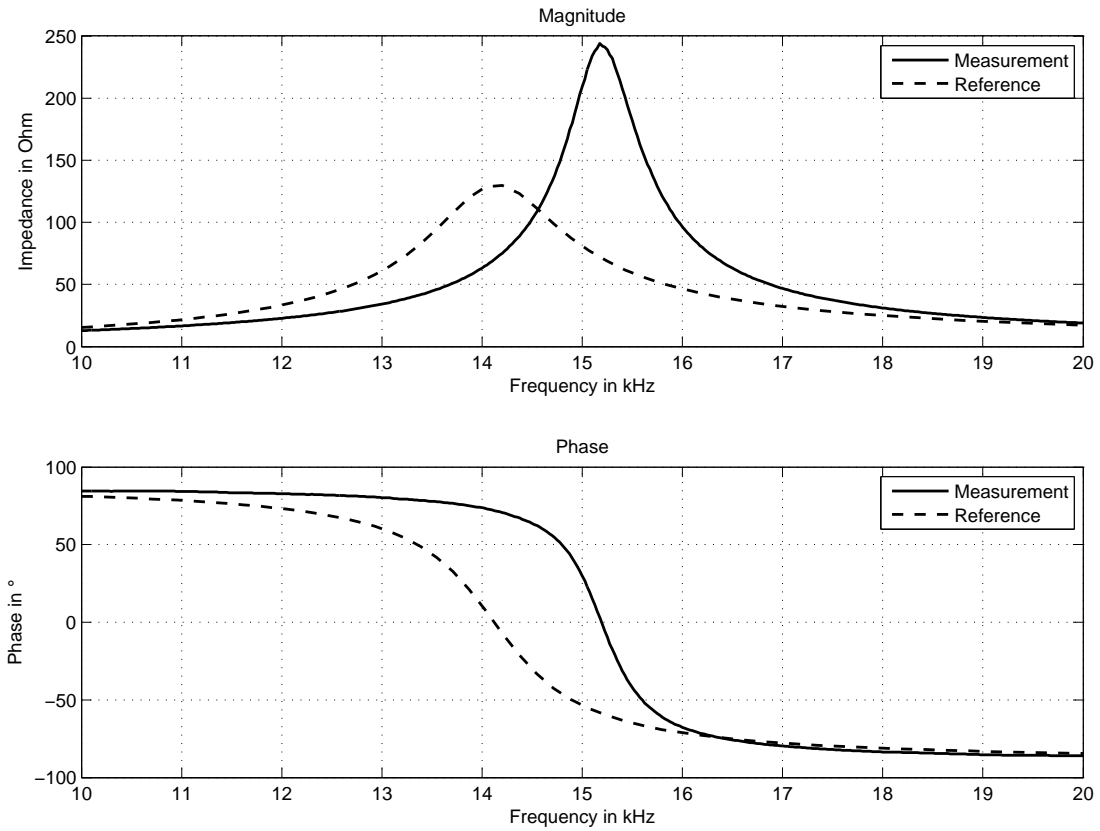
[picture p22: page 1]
Magnitude; Measurement Reference; Phase in °; Phase

Impedance in Ohm

Frequency in kHz

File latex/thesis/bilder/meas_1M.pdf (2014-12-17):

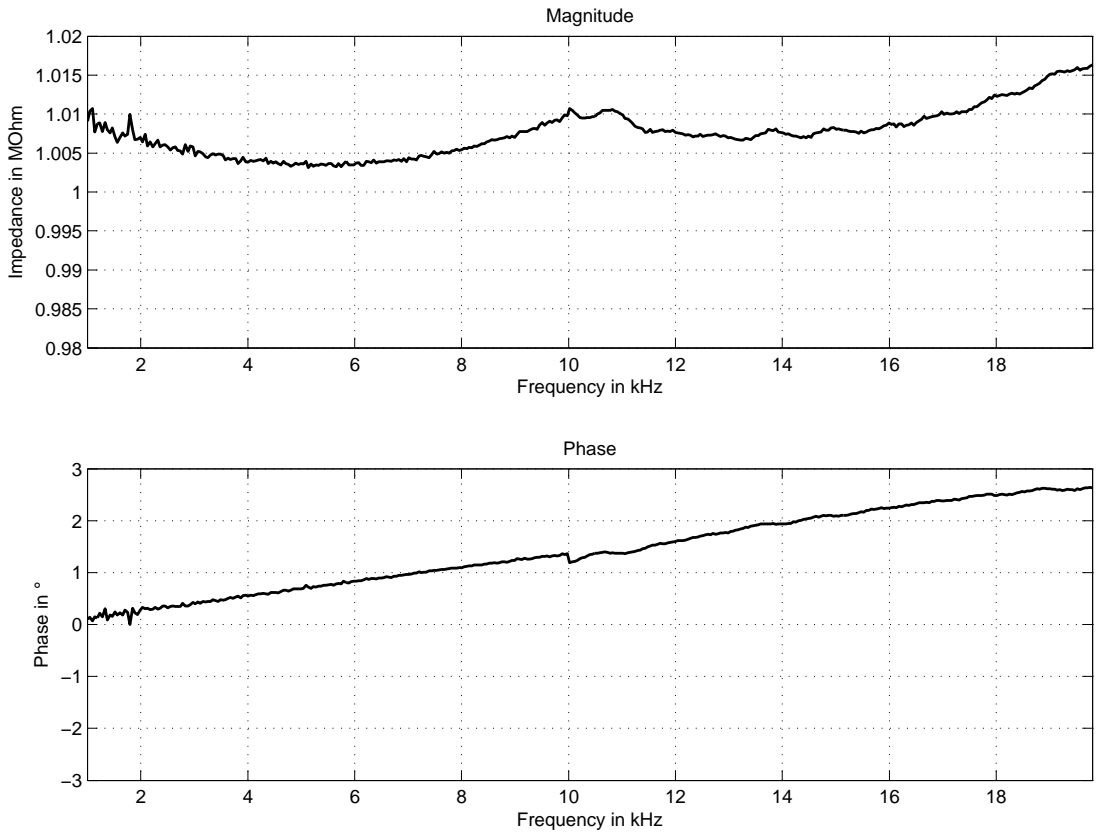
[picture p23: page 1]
Magnitude; Phase in °; Phase

Impedance in MOhm

Frequency in kHz

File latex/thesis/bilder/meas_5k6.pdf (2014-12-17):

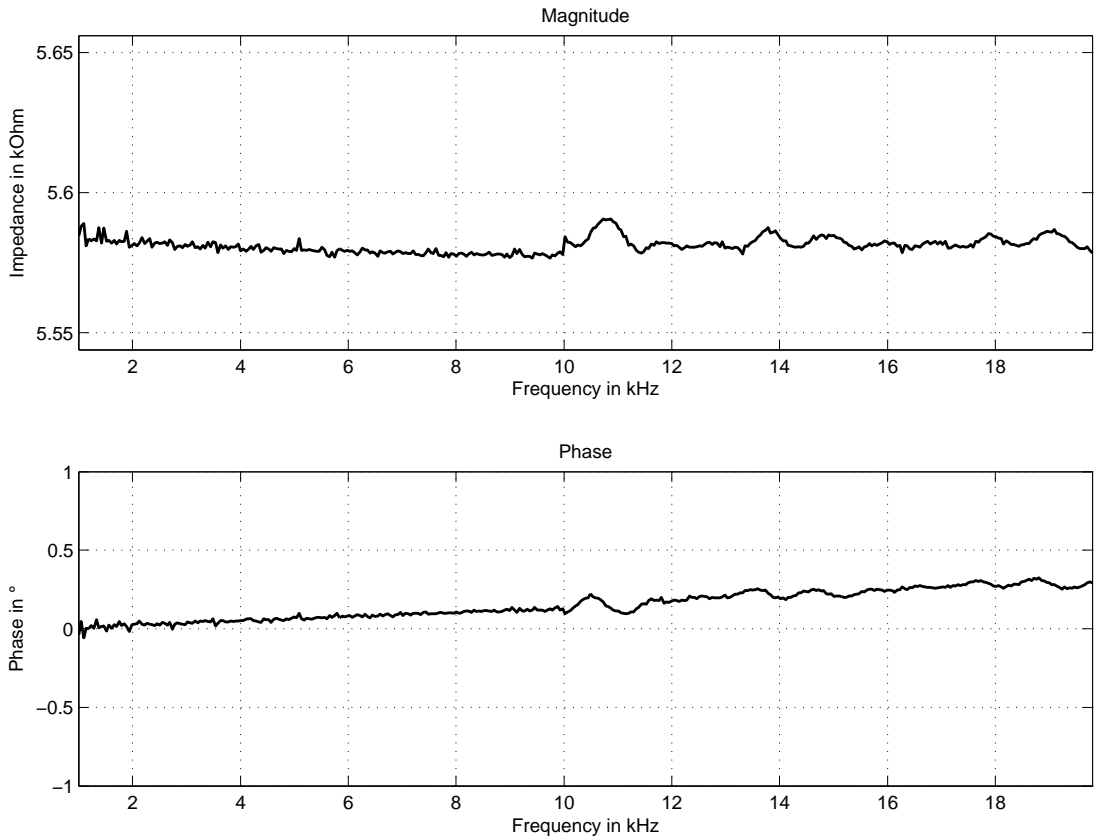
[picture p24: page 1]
Magnitude; Phase in °; Phase

Impedance in kOhm

Frequency in kHz

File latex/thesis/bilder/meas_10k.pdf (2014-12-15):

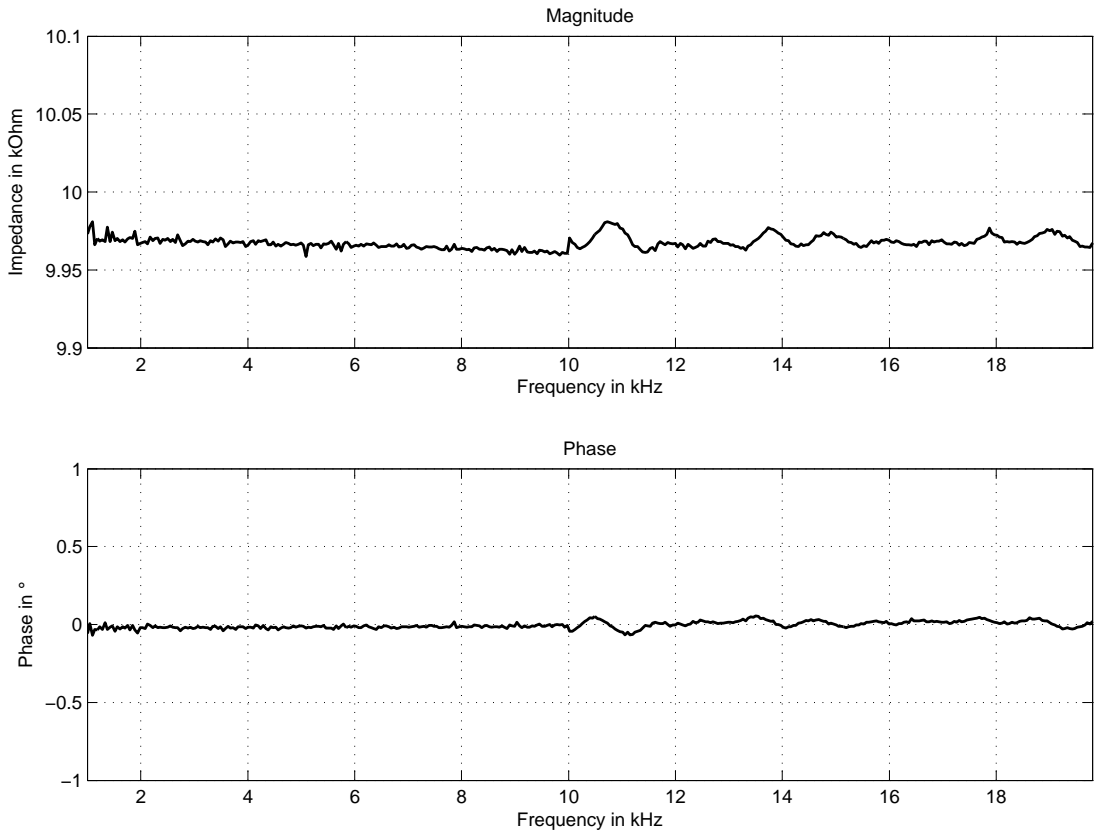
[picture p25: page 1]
Magnitude; Phase in °; Phase

Impedance in kOhm

Frequency in kHz

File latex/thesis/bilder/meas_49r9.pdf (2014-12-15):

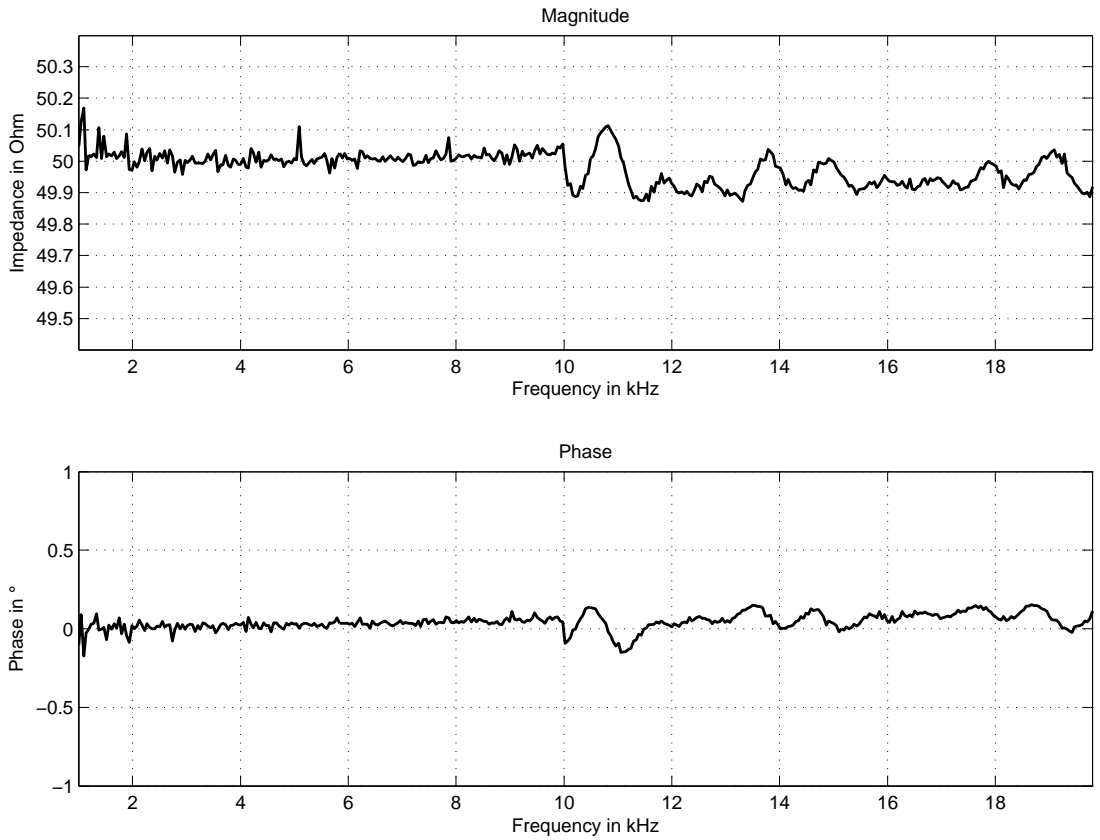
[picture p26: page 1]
Magnitude; Phase in °; Phase

Impedance in Ohm

Frequency in kHz

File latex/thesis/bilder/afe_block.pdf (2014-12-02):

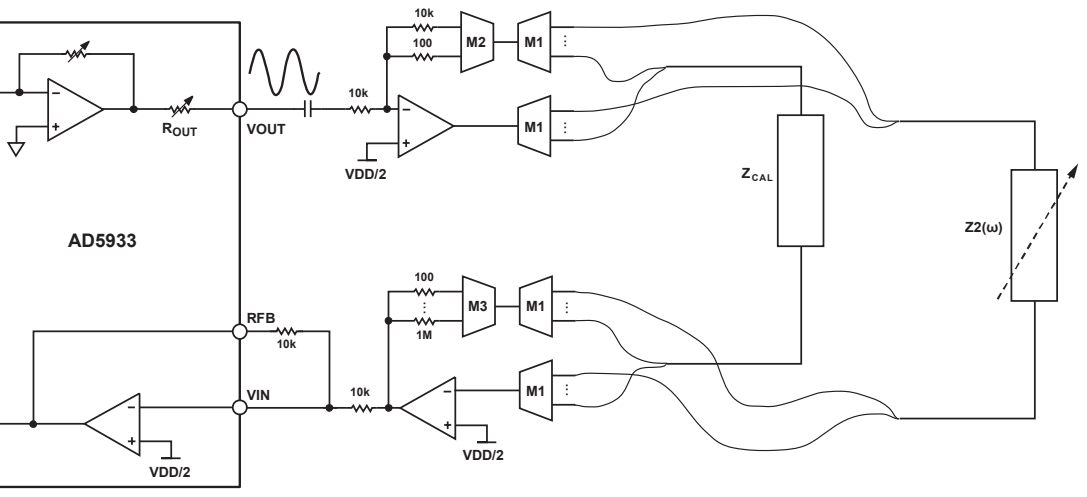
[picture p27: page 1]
VDD; ZCAL

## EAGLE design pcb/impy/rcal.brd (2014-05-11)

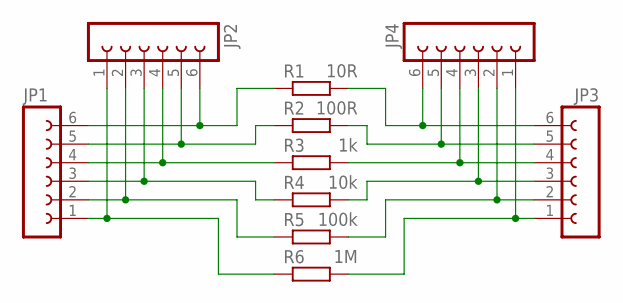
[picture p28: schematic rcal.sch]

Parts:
JP1, JP2, JP3, JP4: FE06-1; FE06
R1: 10R; R0805
R2: 100R; R0805
R3: 1k; R0805
R4: 10k; R0805
R5: 100k; R0805
R6: 1M; R0805

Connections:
unnamed: JP1.6, JP2.6, R1.1
unnamed: JP1.5, JP2.5, R2.1
unnamed: JP1.4, JP2.4, R3.1
unnamed: JP1.3, JP2.3, R4.1
unnamed: JP1.2, JP2.2, R5.1
unnamed: JP1.1, JP2.1, R6.1
unnamed: JP3.6, JP4.6, R1.2
unnamed: JP3.5, JP4.5, R2.2
unnamed: JP3.4, JP4.4, R3.2
unnamed: JP3.3, JP4.3, R4.2
unnamed: JP3.2, JP4.2, R5.2
unnamed: JP3.1, JP4.1, R6.2

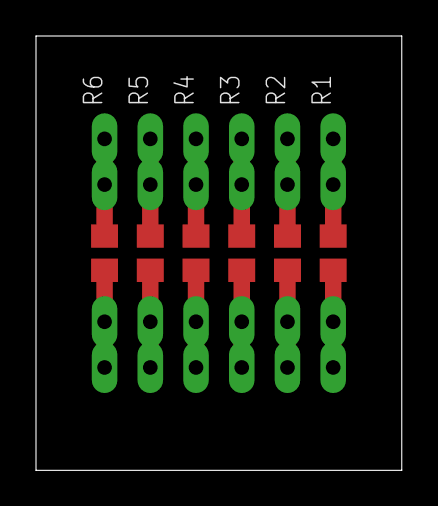
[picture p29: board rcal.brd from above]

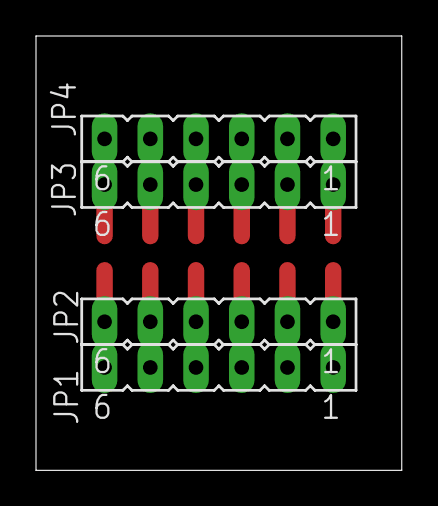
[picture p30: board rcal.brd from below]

Board: 2 copper layers, 20.3 x 24.1 mm, 10 parts (4 on the bottom side), 12 nets.

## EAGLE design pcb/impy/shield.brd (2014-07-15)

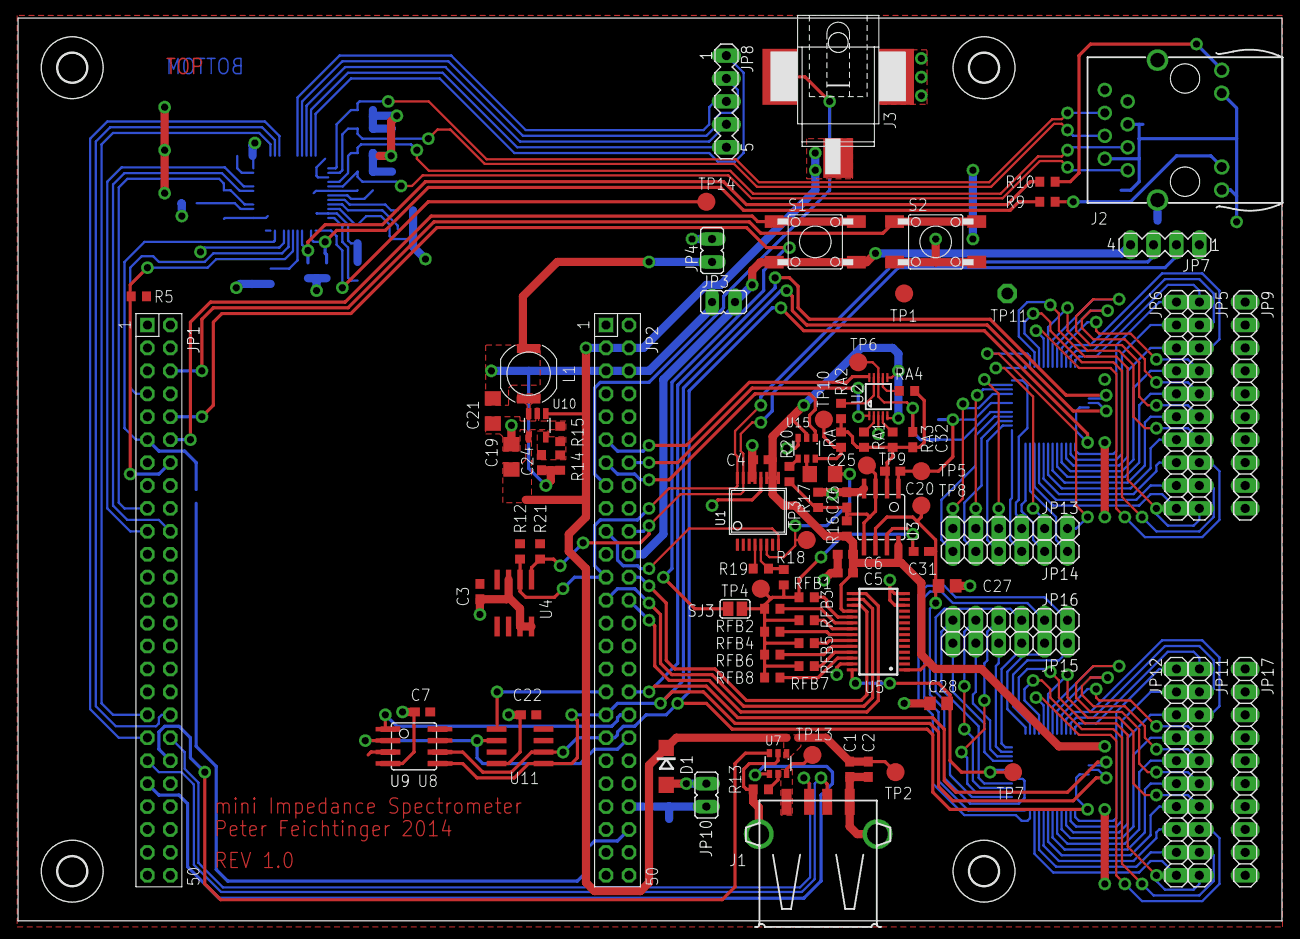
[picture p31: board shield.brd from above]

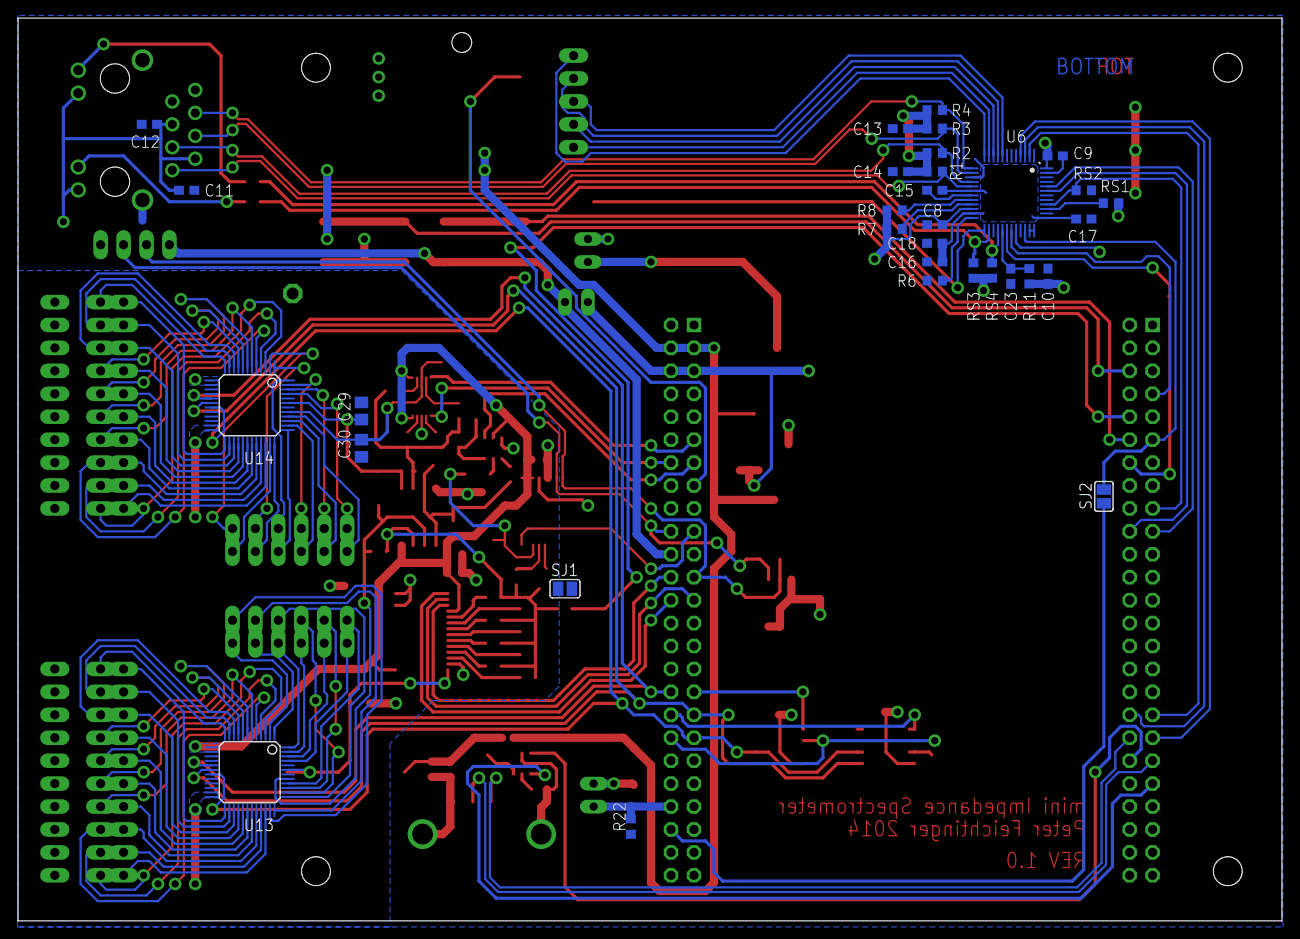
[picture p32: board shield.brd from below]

Board: 2 copper layers, 140.0 x 100.0 mm, 129 parts (32 on the bottom side), 154 nets.

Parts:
C1, C3, C4, C5, C7, C8, C9, C10, C11, C12, C13, C14, C16, C17, C18, C22, C23: 100n; C0603
C2, C6, C15: 10u; C0603
C19: 10u; C3216
C20, C31, C32: N/A; C0603
C21: 10u LowESR; C3216
C24: 22p; C0603
C25: 100u; C1206
C26: 1n; C0603
C27, C28, C29, C30: N/A; C0805
D1: STPS1L30A; DO214AC
J1: USB-2410-06
J2: SI-60062-F
J3: 5V; JACK-SMD2.5
JP1: P1; 2X25-F
JP2: P2; 2X25-F
JP3: Idd; JP1
JP4: Icc; JP1
JP5: FORCE_OUT; 1X10
JP6: SENSE_OUT; 1X10
JP7: I2C; MA04-1
JP8: JTAG; MA05-1
JP9, JP17: GND; 1X10
JP10: VBUS; JP1
JP11: FORCE_IN; 1X10
JP12: SENSE_IN; 1X10
JP13: CAL_FORCE_OUT; 1X06
JP14: CAL_SENSE_OUT; 1X06
JP15: CAL_FORCE_IN; 1X06
JP16: CAL_SENSE_IN; 1X06
L1: A916CY-8R2M; D63CB
R1, R2, R3, R4: 51R; R0603
R5: 1k5; R0603
R6: 4k87 1%; R0603
R7, R8, R11, R16, R17: 2k2; R0603
R9, R10: 150R; R0603
R12, R21: 3k9; R0603
R13: 510R; R0603
R14: 680k 1%; R0603
R15: 150k 1%; R0603
R18, R19, R22: 10k; R0603
R20: 10; R0603
RA, RA1: 10k; R0603
RA2: 100; R0603
RA3, RA4: N/A; R0603
RFB1: 100R; R0603
RFB2: 1k; R0603
RFB3: 10k; R0603
RFB4: 100k; R0603
RFB5: 1M; R0603
RFB6, RFB7, RFB8: N/A; R0603
RS1, RS2, RS3, RS4: 2k2; R0603
S1, S2: FSM4JSMATR; FSM
SJ1: GND; SJ
SJ2: ETH_CLK; SJ
SJ3: OVFL; SJ
TP1, TP2, TP3, TP4, TP5, TP6, TP7, TP8, TP9, TP10, TP13, TP14: TPTP20R; TP20R
TP11: TPPAD1-13; P1-13
U1: AD5933YRS; SSOP16
U2: ADG704BRM; MSOP10
U3: AD8656ARZ; SOIC8
U4: M24C08WMN; SO8
U5: ADG706BRU; TSSOP28
U6: DP83848I; LQFP48
U7: MIC2009A-1YM6; SOT23-6
U8: AT25DF081A-SS; SO8
U9: SST25VF080B-80-4I-S2; SOIC8
U10: LTC3406AB; TSOT23-5
U11: 23LCV1024-I/SN; SO8
U13, U14: ADG725BSU; TQFP48
U15: ADG819BRT; SOT23-6
U$1, U$2, U$3, U$4: 3,2

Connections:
!RST: JP1.6, S2.1, S2.2
+3V3: C21.1, C24.1, JP2.5, JP2.6, JP3.1, JP4.2, L1.2, R14.2
+5V: C1.1, C2.1, C19.1, D1.C, J3.1, JP2.3, JP2.4, TP2.TP, U7.1, U10.1, U10.4
AGND: C4.2, C5.2, C6.2, C26.1, C27.2, C28.1, C29.2, C30.1, JP9.1, JP9.2, JP9.3, JP9.4, JP9.5, JP9.6, JP9.7, JP9.8, JP9.9, JP9.10, JP17.1, JP17.2, JP17.3, JP17.4, JP17.5, JP17.6, JP17.7, JP17.8, JP17.9, JP17.10, R17.1, SJ1.1, TP11.TP, U1.13, U1.14, U2.3, U3.4, U5.12, U5.14, U5.27, U13.23, U13.24, U14.23, U14.24, U15.3
ETH_CLK: JP1.11, SJ2.1, U6.34
GND: C1.2, C2.2, C3.2, C7.2, C8.2, C9.2, C10.2, C11.2, C12.2, C13.1, C14.2, C15.1, C16.1, C17.1, C18.1, C19.2, C21.2, C22.2, C23.2, J1.4, J1.S1, J1.S2, J2.8, J2.S1, J2.S2, J3.2, JP1.1, JP1.2, JP1.49, JP1.50, JP2.1, JP2.2, JP2.49, JP2.50, JP7.1, R6.1, R13.1, R15.1, R22.1, RS2.2, S2.3, S2.4, SJ1.2, U1.12, U4.3, U4.4, U4.7, U6.15, U6.19, U6.35, U6.36, U6.47, U7.2, U8.4, U9.4, U10.2, U11.4
unnamed: C31.1, R18.2, RFB1.2, RFB2.2, RFB3.2, RFB4.2, RFB5.2, RFB6.2, RFB7.2, RFB8.2, SJ3.2, TP4.TP, U3.7
unnamed: RA.2, TP10.TP, U15.6
unnamed: C20.1, C32.1, RA.1, RA1.1, RA2.1, RA3.1, RA4.1, U3.2
unnamed: RA3.2, U2.4
unnamed: RA4.2, U2.7
unnamed: RFB1.1, U5.19
unnamed: RFB2.1, U5.20
unnamed: RFB3.1, U5.21
unnamed: RFB4.1, U5.22
unnamed: RFB5.1, U5.23
unnamed: RFB6.1, U5.24
unnamed: C27.1, C31.2, TP8.TP, U3.6, U13.41
unnamed: C28.2, TP7.TP, U5.28, U13.43
unnamed: C20.2, C29.1, TP5.TP, U3.1, U14.43
unnamed: C30.2, C32.2, TP6.TP, U2.8, U14.41
unnamed: JP12.1, U13.25
unnamed: JP12.2, U13.26
unnamed: JP12.3, U13.27
unnamed: JP12.4, U13.28
unnamed: J2.CY, R9.2
unnamed: RS1.2, U6.39
unnamed: R9.1, RS3.2, U6.26
unnamed: R10.1, RS4.2, U6.28
unnamed: C15.2, C16.2, C17.2, C18.2, U6.18, U6.23, U6.37
unnamed: J2.CG, R10.2
unnamed: J1.1, TP13.TP, U7.6
unnamed: JP8.1, U6.12
unnamed: JP8.2, U6.9
unnamed: JP8.3, U6.8
unnamed: JP8.4, U6.10
unnamed: JP8.5, U6.11
unnamed: C23.1, R11.1, U6.29
unnamed: R6.2, U6.24
unnamed: R8.1, U6.20
unnamed: R7.1, U6.21
unnamed: D1.A, JP10.2
unnamed: R13.2, U7.5
unnamed: C24.2, R14.1, R15.2, U10.5
unnamed: L1.1, U10.3
unnamed: JP12.5, U13.29
unnamed: JP12.6, U13.30
unnamed: JP12.7, U13.31
unnamed: JP12.8, U13.32
unnamed: JP12.9, U13.33
unnamed: JP12.10, U13.34
unnamed: JP11.1, U13.12
unnamed: JP11.2, U13.11
unnamed: JP11.3, U13.10
unnamed: JP11.4, U13.9
unnamed: JP11.5, U13.8
unnamed: JP11.6, U13.7
unnamed: JP11.7, U13.6
unnamed: JP11.8, U13.5
unnamed: JP11.9, U13.4
unnamed: JP11.10, U13.3
unnamed: JP5.1, U14.12
unnamed: JP5.2, U14.11
unnamed: JP5.3, U14.10
unnamed: JP5.4, U14.9
unnamed: JP5.5, U14.8
unnamed: JP5.6, U14.7
unnamed: JP5.7, U14.6
unnamed: JP5.8, U14.5
unnamed: JP5.9, U14.4
unnamed: JP5.10, U14.3
unnamed: JP6.1, U14.25
unnamed: JP6.2, U14.26
unnamed: JP6.3, U14.27
unnamed: JP6.4, U14.28
unnamed: JP6.5, U14.29
unnamed: JP6.6, U14.30
unnamed: JP6.7, U14.31
unnamed: JP6.8, U14.32
unnamed: JP6.9, U14.33
unnamed: JP6.10, U14.34
unnamed: JP13.1, U14.2
unnamed: JP13.2, U14.1
unnamed: JP13.3, U14.48
unnamed: JP13.4, U14.47
unnamed: JP13.5, U14.46
unnamed: JP13.6, U14.45
unnamed: JP14.1, U14.35
unnamed: JP14.2, U14.36
unnamed: JP14.3, U14.37
unnamed: JP14.4, U14.38
unnamed: JP14.5, U14.39
unnamed: JP14.6, U14.40
unnamed: JP15.1, U13.2
unnamed: JP15.2, U13.1
unnamed: JP15.3, U13.48
unnamed: JP15.4, U13.47
unnamed: JP15.5, U13.46
unnamed: JP15.6, U13.45
unnamed: JP16.1, U13.35
unnamed: JP16.2, U13.36
unnamed: JP16.3, U13.37
unnamed: JP16.4, U13.38
unnamed: JP16.5, U13.39
unnamed: JP16.6, U13.40
unnamed: RA2.2, U2.9
unnamed: RA1.2, U2.2
unnamed: RFB7.1, U5.25
unnamed: RFB8.1, U5.26
unnamed: TP14.TP, U6.25
unnamed: C25.1, U15.5
unnamed: R20.1, U15.4
PA0: JP1.12, S1.1, S1.2
PA2: JP1.14, R5.1, U6.30
PA7: JP1.17, RS2.1, U6.40
PA9: JP2.44, JP10.1, R22.2
PB4: JP2.25, U5.16
PB5: JP2.26, U5.15
PB6: JP2.23, JP7.3, R12.1, U1.16, U4.6
PB7: JP2.24, U5.17
PB8: JP2.19, U1.8
PB9: JP2.20, JP7.2, R21.1, U1.15, U4.5
PB11: JP1.35, U6.2
PB12: JP1.36, U6.3
PB13: JP1.37, U6.4
PC1: JP1.7, U6.31
PC2: JP1.10, SJ3.1
PC4: JP1.20, U6.43
PC5: JP1.19, U6.44
PC9: JP2.46, SJ2.2
PC10: JP2.37, U8.6, U9.6, U11.6, U13.19, U14.19
PC11: JP2.38, U8.2, U9.2, U11.2
PC12: JP2.35, U8.5, U9.5, U11.5, U13.18, U14.18
PD0: JP2.36, U8.1, U9.1
PD1: JP2.33, U11.1
PD2: JP2.34, U13.17, U14.17
PD8: JP1.40, U7.3
PD9: JP1.41, U7.4
PE2: J3.3, JP2.15
PE4: JP2.13, U15.1
PE5: JP2.14, U2.1
PE6: JP2.11, U2.10
RD_N: J2.6, R4.1, U6.13
RD_P: J2.4, R3.1, U6.14
RFB: R19.1, U1.4
TD_N: J2.3, R2.1, U6.16
TD_P: J2.1, R1.1, U6.17
USB_N: J1.2, JP1.38
USB_P: J1.3, JP1.39
VCC: C3.1, C4.1, C5.1, C6.1, C7.1, C8.1, C9.1, C10.1, C11.1, C12.1, C13.2, C14.1, C22.1, J2.2, J2.5, J2.AG, J2.AY, JP4.1, R1.2, R2.2, R3.2, R4.2, R5.2, R7.2, R8.2, R11.2, R12.2, R16.2, R21.2, RS1.1, RS3.1, RS4.1, TP1.TP, U1.9, U1.10, U1.11, U2.5, U2.6, U3.8, U4.8, U5.1, U5.18, U6.22, U6.32, U6.48, U8.3, U8.7, U8.8, U9.3, U9.7, U9.8, U11.7, U11.8, U13.13, U13.14, U14.13, U14.14, U15.2
VCC/2: C26.2, R16.1, R17.2, R20.2, TP9.TP, U3.3, U3.5
VDD: JP2.22, JP3.2, JP7.4, S1.3, S1.4
VIN: R18.1, R19.2, U1.5
VOUT: C25.2, TP3.TP, U1.6

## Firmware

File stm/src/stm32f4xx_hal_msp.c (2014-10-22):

/**
 * @file    stm32f4xx_hal_msp.c
 * @author  Peter Feichtinger
 * @date    14.04.2014
 * @brief   Provides MSP initialization code.
 */

// Includes -------------------------------------------------------------------
#include "stm32f4xx_hal.h"

// Exported functions ---------------------------------------------------------

/**
 * Initializes the I2C MSP.
 * 
 * @param hi2c I2C handle
 */
void HAL_I2C_MspInit(I2C_HandleTypeDef* hi2c) {
    GPIO_InitTypeDef GPIO_InitStruct;
    if(hi2c->Instance == I2C1) {
        __I2C1_CLK_ENABLE();
        
        /*
         * GPIO configuration:
         *  PB6: I2C1_SCL
         *  PB9: I2C1_SDA
         */
        GPIO_InitStruct.Pin = GPIO_PIN_6 | GPIO_PIN_9;
        GPIO_InitStruct.Mode = GPIO_MODE_AF_OD;
        GPIO_InitStruct.Pull = GPIO_NOPULL;
        GPIO_InitStruct.Speed = GPIO_SPEED_LOW;
        GPIO_InitStruct.Alternate = GPIO_AF4_I2C1;
        HAL_GPIO_Init(GPIOB, &GPIO_InitStruct);
        
        // Set I2C interrupt to the lowest priority
        HAL_NVIC_SetPriority(I2C1_EV_IRQn, 10, 0);
        NVIC_EnableIRQ(I2C1_EV_IRQn);
    }
}

/**
 * De-initializes the I2C MSP.
 * 
 * @param hi2c I2C handle
 */
void HAL_I2C_MspDeInit(I2C_HandleTypeDef* hi2c) {
    if(hi2c->Instance == I2C1) {
        __I2C1_CLK_DISABLE();
        HAL_GPIO_DeInit(GPIOB, GPIO_PIN_6 | GPIO_PIN_9);
        NVIC_DisableIRQ(I2C1_EV_IRQn);
    }
}

/**
 * Initializes the SPI MSP.
 * 
 * @param hspi SPI handle
 */
void HAL_SPI_MspInit(SPI_HandleTypeDef* hspi) {
    GPIO_InitTypeDef GPIO_InitStruct;
    if(hspi->Instance == SPI3) {
        __SPI3_CLK_ENABLE();
        
        /*
         * GPIO configuration:
         *  PC10: SPI3_SCK
         *  PC11: SPI3_MISO
         *  PC12: SPI3_MOSI
         */
        GPIO_InitStruct.Pin = GPIO_PIN_10 | GPIO_PIN_11 | GPIO_PIN_12;
        GPIO_InitStruct.Mode = GPIO_MODE_AF_PP;
        GPIO_InitStruct.Pull = GPIO_NOPULL;
        GPIO_InitStruct.Speed = GPIO_SPEED_HIGH;
        GPIO_InitStruct.Alternate = GPIO_AF6_SPI3;
        HAL_GPIO_Init(GPIOC, &GPIO_InitStruct);
        
        // Set SPI interrupt to the lowest priority
        HAL_NVIC_SetPriority(SPI3_IRQn, 10, 0);
        NVIC_EnableIRQ(SPI3_IRQn);
    }
}

/**
 * De-initializes the SPI MSP.
 * 
 * @param hspi SPI handle
 */
void HAL_SPI_MspDeInit(SPI_HandleTypeDef* hspi) {
    if(hspi->Instance == SPI3) {
        __SPI3_CLK_DISABLE();
        HAL_GPIO_DeInit(GPIOD, GPIO_PIN_0 | GPIO_PIN_1 | GPIO_PIN_2);
        HAL_GPIO_DeInit(GPIOC, GPIO_PIN_10 | GPIO_PIN_11 | GPIO_PIN_12);
        NVIC_DisableIRQ(SPI3_IRQn);
    }
}

/**
 * Initializes the TIM MSP.
 * 
 * @param htim TIM handle
 */
void HAL_TIM_Base_MspInit(TIM_HandleTypeDef* htim) {
    GPIO_InitTypeDef GPIO_InitStruct;
    if(htim->Instance == TIM3) {
        __TIM3_CLK_ENABLE();
        HAL_NVIC_SetPriority(TIM3_IRQn, 7, 0);
        NVIC_EnableIRQ(TIM3_IRQn);
        
    } else if(htim->Instance == TIM10) {
        __TIM10_CLK_ENABLE();
        
        /*
         * GPIO configuration:
         *  PB8: TIM10_CH1
         */
        GPIO_InitStruct.Pin = GPIO_PIN_8;
        GPIO_InitStruct.Mode = GPIO_MODE_AF_PP;
        GPIO_InitStruct.Pull = GPIO_NOPULL;
        GPIO_InitStruct.Speed = GPIO_SPEED_FAST;
        GPIO_InitStruct.Alternate = GPIO_AF3_TIM10;
        HAL_GPIO_Init(GPIOB, &GPIO_InitStruct);
    }
}

/**
 * De-initializes the TIM MSP.
 * 
 * @param htim TIM handle
 */
void HAL_TIM_Base_MspDeInit(TIM_HandleTypeDef* htim) {
    if(htim->Instance == TIM3) {
        __TIM3_CLK_DISABLE();
        NVIC_DisableIRQ(TIM3_IRQn);
        
    } else if(htim->Instance == TIM10) {
        __TIM10_CLK_DISABLE();
        HAL_GPIO_DeInit(GPIOB, GPIO_PIN_8);
    }
}

// ----------------------------------------------------------------------------

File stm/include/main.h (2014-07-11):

/**
 * @file    main.h
 * @author  Peter Feichtinger
 * @date    13.04.2014
 * @brief   Main header file.
 */

#ifndef MAIN_H_
#define MAIN_H_

// Includes -------------------------------------------------------------------
#include <stdint.h>
#include "stm32f4xx_hal.h"
#include "mx_init.h"
#include "console.h"
#include "ad5933.h"
#include "eeprom.h"

// Exported type definitions --------------------------------------------------
/**
 * The possible outcomes of a command.
 */
typedef enum
{
    BOARD_OK = 0,       //!< Indicates success
    BOARD_BUSY,         //!< Indicates that the board is currently busy and settings cannot be changed
    BOARD_ERROR         //!< Indicates an error condition
} Board_Error;

/**
 * The possible sources for a temperature measurement.
 */
typedef enum
{
    TEMP_AD5933         //!< AD5933 internal chip temperature
} Board_TemperatureSource;

/**
 * Contains status information for the board.
 */
typedef struct
{
    AD5933_Status ad_status;    //!< Status code of the AD5933 driver
    uint16_t point;             //!< If a measurement is running, the number of data points already measured
    uint16_t totalPoints;       //!< The number of frequency steps to be measured
    uint8_t autorange;          //!< Whether autoranging is enabled
    uint8_t interrupted;        //!< Whether the last measurement was interrupted (false if a measurement is running)
    uint8_t validGainFactor;    //!< Whether a valid gain factor for the current range settings is present
    uint8_t validData;          //!< Whether valid measurement data is present
} Board_Status;

// Constants ------------------------------------------------------------------
#define BOARD_VERSION                   "1.0"

#define LED_PORT                        GPIOD
#define LED_ORANGE                      GPIO_PIN_13
#define LED_GREEN                       GPIO_PIN_12
#define LED_RED                         GPIO_PIN_14
#define LED_BLUE                        GPIO_PIN_15

#define BUTTON_PORT						GPIOA					//!< User button GPIO port
#define BUTTON_PIN						GPIO_PIN_0				//!< User button GPIO pin (active high)

#define SWITCH_MAIN_PORT				GPIOC					//!< Main power switch (Icc) GPIO port
#define SWITCH_MAIN_PIN					GPIO_PIN_15				//!< Main power switch (Icc) GPIO pin (active high)

#define SWITCH_USB_PORT					GPIOD					//!< USB host power switch GPIO port
#define SWITCH_USB_PIN					GPIO_PIN_8				//!< USB host power switch GPIO pin (active high)

/**
 * The maximum port number that can be used for measurements.
 */
#define PORT_MAX                        9

/**
 * The first calibration port number
 */
#define CAL_PORT_MIN                    10

/**
 * Timeout in ms for SPI communication
 */
#define BOARD_SPI_TIMEOUT               10

/**
 * @defgroup BOARD_SPI_SS_GPIO SPI Slave Select GPIO Definition
 * @{
 */
#define BOARD_SPI_SS_GPIO_PORT          GPIOD
#define BOARD_SPI_SS_GPIO_FLASH         GPIO_PIN_0
#define BOARD_SPI_SS_GPIO_SRAM          GPIO_PIN_1
#define BOARD_SPI_SS_GPIO_MUX           GPIO_PIN_2
/** @} */

/**
 * @defgroup ADG725 Communication Definition for the ADG725
 * @{
 */
#define ADG725_MASK_PORT                ((uint8_t)0x0F)
#define ADG725_CHIP_ENABLE_NOT          ((uint8_t)0x80)
#define ADG725_CHIP_CSA_NOT             ((uint8_t)0x40)
#define ADG725_CHIP_CSB_NOT             ((uint8_t)0x20)
/** @} */

/**
 * Whether the E2 pin on the EEPROM chip is pulled high.
 */
#define EEPROM_E2_PIN_SET               0

/**
 * The time after which changed settings are written to the EEPROM in ms.
 */
#define EEPROM_WRITE_INTERVAL           1000

// Exported variables ---------------------------------------------------------
extern USBD_HandleTypeDef hUsbDevice;
extern I2C_HandleTypeDef hi2c1;
extern SPI_HandleTypeDef hspi3;
extern TIM_HandleTypeDef htim3;
extern TIM_HandleTypeDef htim10;
extern CRC_HandleTypeDef hcrc;
extern uint8_t board_has_eeprom;
extern EEPROM_ConfigurationBuffer board_config;

// Exported functions ---------------------------------------------------------
Board_Error Board_SetStartFreq(uint32_t freq);
Board_Error Board_SetStopFreq(uint32_t freq);
Board_Error Board_SetFreqSteps(uint16_t steps);
Board_Error Board_SetSettlingCycles(uint16_t cycles, uint8_t multiplier);
Board_Error Board_SetVoltageRange(uint16_t voltage);
Board_Error Board_SetPGA(uint8_t enable);
Board_Error Board_SetAutorange(uint8_t enable);
Board_Error Board_SetFeedback(uint32_t ohms);
Board_Error Board_SetAverages(uint16_t value);

uint32_t Board_GetStartFreq(void);
uint32_t Board_GetStopFreq(void);
uint16_t Board_GetFreqSteps(void);
uint16_t Board_GetSettlingCycles(void);
const AD5933_RangeSettings* Board_GetRangeSettings(void);
uint8_t Board_GetAutorange(void);
uint16_t Board_GetAverages(void);

void Board_GetStatus(Board_Status *result);
void Board_Reset(void);
void Board_Standby(void);
const AD5933_ImpedancePolar* Board_GetDataPolar(uint32_t *count);
const AD5933_ImpedanceData* Board_GetDataRaw(uint32_t *count);
const AD5933_GainFactor* Board_GetGainFactor(void);
Board_Error Board_StartSweep(uint8_t port);
Board_Error Board_StopSweep(void);
uint8_t Board_GetPort(void);
Board_Error Board_MeasureSingleFrequency(uint8_t port, uint32_t freq, AD5933_ImpedancePolar *result);
Board_Error Board_MeasureTemperature(Board_TemperatureSource what);
Board_Error Board_Calibrate(uint32_t ohms);

void MarkSettingsDirty(void);
void WriteConfiguration(void);


// ----------------------------------------------------------------------------

#endif /* MAIN_H_ */

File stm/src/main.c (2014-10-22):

/**
 * @file    main.c
 * @author  Peter Feichtinger
 * @date    13.04.2014
 * @brief   Main file for the impedance spectrometer firmware.
 */

// Includes -------------------------------------------------------------------
#include <math.h>
#include "main.h"

// Private function prototypes ------------------------------------------------
static void SetDefaults(void);
static void UpdateSettings(void);
static void InitFromEEPROM(void);
static void Handle_TIM3_AD5933(void);
static void Handle_TIM3_EEPROM(void);

// Variables ------------------------------------------------------------------
USBD_HandleTypeDef hUsbDevice;
I2C_HandleTypeDef hi2c1;
SPI_HandleTypeDef hspi3;
TIM_HandleTypeDef htim3;
TIM_HandleTypeDef htim10;
CRC_HandleTypeDef hcrc;

// Default board configuration
uint8_t board_has_eeprom = 0;
EEPROM_ConfigurationBuffer board_config =
{
    .peripherals = {
        .sram = 0,
        .flash = 0,
        .eth = 0,
        .usbh = 0,
        .reserved = 0
    },
    .attenuations = { 1, 100, 0, 0 },
    .feedback_resistors = { 100, 1000, 10000, 100000, 1000000, 0, 0, 0 },
    .calibration_values = { 10, 100, 1000, 10000, 100000, 1000000 },
    .coupling_tau = 110,
    .eth_mac = { 0x11, 0x00, 0xAA, 0x00, 0x00, 0x00 },
    .sram_size = 0,
    .flash_size = 0,
    .reserved = { 0 },
    .checksum = 0
};
static volatile uint8_t config_dirty = 0;

// Settings storage
static EEPROM_SettingsBuffer settings;
static volatile uint8_t settings_dirty = 0;
static volatile uint32_t settings_dirty_tick;

// AD5933 driver values
static AD5933_Sweep sweep;
static AD5933_RangeSettings range;
static uint32_t stopFreq;
static uint8_t lastPort;
static uint8_t autorange;       // Whether autoranging should be enabled for the next sweep

// Data
static AD5933_ImpedanceData bufData[AD5933_MAX_NUM_INCREMENTS + 1];
static uint8_t validData = 0;
static AD5933_ImpedancePolar bufPolar[AD5933_MAX_NUM_INCREMENTS + 1];
static uint8_t validPolar = 0;
static AD5933_GainFactor dataGainFactor;    // Gain factor for valid raw data
static uint32_t pointCount = 0;
static uint8_t interrupted = 0;
static AD5933_GainFactorData gainData;
static AD5933_GainFactor gainFactor;        // Current gain factor, could have changed since the measurement finished
static uint8_t validGain = 0;               // Whether gainFactor is valid for the current sweep parameters
static float temp;                          // Result from temperature measurements

// main and Interrupt handlers ------------------------------------------------

__attribute__((noreturn))
int main(int argc __attribute__((unused)), char* argv[] __attribute__((unused))) {
    // At this stage the system clock should have already been configured at high speed.
    MX_Init();
    Console_Init();
    SetDefaults();
    
    if(EE_Init(&hi2c1, &hcrc, EEPROM_E2_PIN_SET) == EE_OK) {
        board_has_eeprom = 1;
        InitFromEEPROM();
    }
    
    AD5933_Init(&hi2c1, &htim10);
    
    // Call configuration dependent initialization functions
    if(board_config.peripherals.eth) {
        MX_Init_Ethernet();
    }
    
    // Start timer for periodic interrupt generation
    HAL_TIM_Base_Start_IT(&htim3);
    
    while(1) {
        // Do stuff.
        HAL_GPIO_TogglePin(LED_PORT, LED_BLUE);
        HAL_Delay(600);
    }
}

/**
 * Calls the appropriate functions for timer period interrupts.
 * 
 * @param htim Timer handle
 */
void HAL_TIM_PeriodElapsedCallback(TIM_HandleTypeDef *htim) {
    if(htim->Instance == TIM3) {
        Handle_TIM3_AD5933();
        Handle_TIM3_EEPROM();
    }
}

/**
 * Handles TIM3 period elapsed event for the AD5933 driver.
 */
static void Handle_TIM3_AD5933(void) {
    static AD5933_Status prevStatus = AD_UNINIT;
    
    AD5933_Status status = AD5933_TimerCallback();
    if(prevStatus == status) {
        return;
    }
    switch(status) {
        case AD_FINISH_IMPEDANCE:
            pointCount = AD5933_GetSweepCount();
            interrupted = 0;
            
            if(prevStatus == AD_MEASURE_IMPEDANCE) {
                validData = 1;
                validPolar = 0;
                dataGainFactor = gainFactor;
            } else if(prevStatus == AD_MEASURE_IMPEDANCE_AUTORANGE) {
                validData = 0;
                validPolar = 1;
            }
            break;
            
        case AD_FINISH_CALIB:
            AD5933_CalculateGainFactor(&gainData, &gainFactor);
            validGain = 1;
            Console_CalibrateCallback();
            break;
            
        case AD_FINISH_TEMP:
            Console_TempCallback(temp);
            break;
            
        default:
            break;
    }
    prevStatus = status;
}

/**
 * Handles TIM3 period elapsed event for the EEPROM driver.
 */
static void Handle_TIM3_EEPROM(void) {
    if(!board_has_eeprom) return;
    
    EE_TimerCallback();
    if(EE_IsBusy()) {
        return;
    }
    if(config_dirty) {
        EE_WriteConfiguration(&board_config);
        config_dirty = 0;
        return;
    }
    if(settings_dirty && HAL_GetTick() - settings_dirty_tick > EEPROM_WRITE_INTERVAL) {
        UpdateSettings();
        EE_WriteSettings(&settings);
        settings_dirty = 0;
        return;
    }
}

// Private functions ----------------------------------------------------------
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

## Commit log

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2014-04-16 * pcb: Add EAGLE project directory (impy) with empty schematic for the shield (impy/shield.sch).
    [shield.sch]
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2014-04-17 * pcb/impy: (shield.sch) Add pin headers and label used pins.
    [shield.sch]
2014-04-17 * pcb/impy: (shield.sch) Add sheet for AD5933 and associated components.
    [shield.sch]
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2014-04-17 * pcb/impy: (shield.sch) Add AD5933 and two more pins.
    [shield.sch]
2014-04-17 * pcb/impy: (shield.sch) Add supply legend, jumpers and connect AD5933 to supply.
    [shield.sch]
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2014-04-17 * pcb/impy: (shield.sch) Add analog multiplexers and calibration and feedback resistors.
    [shield.sch]
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2014-04-17 * pcb/impy: (shield.sch) Add sheet for memory and M24C08 to that sheet.
    [shield.sch]
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2014-04-18 * pcb/impy: (shield.sch) Update parts from parts.lbr library and fix IC name prefixes.
    [shield.sch]
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2014-04-18 * pcb/impy: (shield.sch) Update M24C08 from parts.lbr library and move stuff around to fit new symbol.
    [shield.sch]
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2014-04-18 * pcb/impy: (shield.sch) Add preliminary values to feedback and calibration resistors.
    [shield.sch]
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2014-04-18 * pcb/impy: (shield.sch) Update parts from parts.lbr library.
    [shield.sch]
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2014-04-19 * pcb/impy: (shield.sch) Update M24C08 from parts.lbr library. Change test impedance connector from AGND to VIN.
    [shield.sch]
2014-04-19 * pcb/impy: (shield.sch) Add AD5933 output buffer.
    [shield.sch]
2014-04-19 * pcb/impy: (shield.sch) Add power supply bypass caps.
    [shield.sch]
2014-04-19 * pcb/impy: (shield.sch) Add sheet for communication related stuff.
    [shield.sch]
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2014-04-19 * pcb/impy: (shield.sch) Add USB A connector.
    [shield.sch]
2014-04-19 * pcb/impy: (shield.sch) Add I2C header and replace impedance pin header with numbered version. (eagle.epf) Add male and female pin header libraries (con-lsta.lbr and con-lstb.lbr).
    [shield.sch]
2014-04-19 * pcb/impy: (shield.sch) Add Ethernet MAC and MagJack.
    [shield.sch]
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2014-04-19 * pcb/impy: (shield.sch) Add USB power switch and signals (PD8, PD9).
    [shield.sch]
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2014-04-19 * pcb/impy: (shield.sch) Add SPI flash memory.
    [shield.sch]
2014-04-19 * pcb/impy: (shield.sch) Add second SPI flash memory with different footprint, so both can be used.
    [shield.sch]
2014-04-19 * pcb/impy: (shield.sch) Move stuff around on the supply page.
    [shield.sch]
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2014-04-19 * pcb/impy: (shield.sch) Add input voltage regulator.
    [shield.sch]
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2014-04-19 * pcb/impy: (shield.sch) Replace pin headers with custom version from parts library. Add some pretty frames to supply sheet.
    [shield.sch]
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2014-04-19 * pcb/impy: (shield.sch) Add SPI SRAM memory. Fix missing connection to bypass cap.
    [shield.sch]
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2014-04-19 * pcb/impy: (shield.sch) Update TC1262 from parts.lbr library.
    [shield.sch]
2014-04-19 * pcb/impy: (shield.sch) Add Ethernet clock link and rename nets. Add pin labels to Ethernet clock pins.
    [shield.sch]
2014-04-19 * pcb/impy: (shield.sch) Add pull-up for MAC reset pin. Add some ERC errors to approved list (unconnected MAC TXD inputs, unused named nets).
    [shield.sch]
2014-04-19 * pcb/impy: (shield.sch) Add values for connectors and jumpers.
    [shield.sch]
2014-04-19 * pcb/impy: (shield.sch) Add solder jumper to separate ETH_CLK from PA1, in case no Ethernet is needed. Add value to GND-AGND jumper.
    [shield.sch]
2014-04-19 * pcb/impy: (shield.sch) Add BOOT0 jumper for possible firmware upgrade option.
    [shield.sch]
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2014-04-19 * pcb/impy: (shield.sch) Add User and Reset buttons. Move voltage regulator.
    [shield.sch]
2014-04-19 * pcb/impy: (shield.sch) Add net classes supply and analog and add appropriate nets.
    [shield.sch]
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2014-04-19 * pcb/impy: (shield.sch) Update from parts.lbr library.
    [shield.sch]
2014-04-19 * pcb/impy: Add board file for the shield (shield.brd) with dimensions of Discovery board.
    [shield.brd]
2014-04-20 * pcb/impy: (shield.sch) Add jumper to use VBUS from Micro USB port for 5V supply.
    [shield.sch]
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2014-04-20 * pcb/impy: (shield.sch) Add DJ power jack and jack detect signal PE2. (shield.brd) Update from schematic and move some stuff around.
    [shield.brd, shield.sch]
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2014-04-21 * pcb/impy: (shield.brd) Group parts by function.
    [shield.brd]
2014-04-21 * pcb/impy: (shield.brd) Fix position of discovery board connectors. Add markers for discovery board jumper feet.
    [shield.brd]
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2014-04-22 * pcb/impy: (shield.sch) Add main power switch and signal (PB10). Add VBUS diode, this allows us to determine whether power comes from the USB device port or somewhere else.
    [shield.brd, shield.sch]
2014-04-22 * pcb/impy: (shield.sch) Replace USB host power switch by MIC2009A-1 and set current limit to 400mA. Fix missing supply class for some nets.
    [shield.brd, shield.sch]
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2014-04-22 * pcb/impy: (shield.sch) Replace LDO by LTC3406 switching regulator.
    [shield.brd, shield.sch]
2014-04-22 * pcb/impy: (shield.sch) Change value of pullup resistor for PHY reset, 2k2 is used quite often so use this one.
    [shield.sch]
2014-04-22 * pcb/impy: (shield.brd) Update from schematic.
    [shield.brd]
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2014-04-23 * pcb/impy: (shield.brd) Move discovery board connectors to align with 25mil grid. Change design rules to IME in house rules.
    [shield.brd]
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2014-04-23 * pcb/impy: (shield.sch) Update MIC2009A-1 from parts.lbr library.
    [shield.sch]
2014-04-23 * pcb/impy: (shield.sch, shield.brd) Change footprints for resistors and capacitors to 0603 and values to E24 where possible.
    [shield.brd, shield.sch]
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2014-04-23 * pcb/impy: (shield.sch, shield.brd) Change VBUS diode to STPS1L30 from parts.lbr library. Change packages for calibration resistors and low ESR capacitor. Change LTC3406 divider resistor values.
    [shield.brd, shield.sch]
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2014-04-25 * pcb/impy: (shield.sch) Add AD5933 clock signal (PB8) and third SPI SS signal (PD2).
    [shield.brd, shield.sch]
2014-04-25 * pcb/impy: (shield.sch) Change whole AD5933 external analog front end.
    The new front end uses 4-wire measurement to eliminate the series resistance of the analog multiplexers and test leads.
    Using four 16:1 multiplexers, up to 10 channels can be used together with 6 calibration resistors.
    The output signal from the AD5933 is AC coupled so as to eliminate the DC bias, which limits the dynamic range.
    With the option of four selectable attenuation values for the AD5933 output voltage, impedances down to about 10 Ohms can be measured, if the chip is also clocked from a slow external source the meas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
    [shield.brd, shield.sch]
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2014-04-30 * pcb/impy: (shield.brd) Layout USB connector. (shield.sch) Fix wrong supply net connection for USB bypass capacitors C1 and C2 (was VCC, should be +5V).
    [shield.brd, shield.sch]
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2014-05-01 * pcb/impy: (shield.sch) Swap around Ethernet jack LED dropper resistors for better routing. (shield.brd) Change layout of Ethernet LEDs.
    [shield.brd, shield.sch]
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2014-05-02 * pcb/impy: (shield.sch) Fix supply of I2C header, should be VDD in case this is supplied from the discovery board or does not match VCC for some other reason.
    [shield.brd, shield.sch]
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2014-05-02 * pcb/impy: (shield.sch) Fix missing ground connection on discovery connector.
    [shield.brd, shield.sch]
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2014-05-04 * pcb/impy: (shield.brd) Fix connection to jumper pins on top layer (cannot solder on top layer). Add missing connection that was previously removed.
    [shield.brd]
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2014-05-04 * pcb/impy: (shield.brd) Fix trace width.
    [shield.brd]
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2014-05-06 * pcb/impy: (shield.sch, shield.brd) Replace surface mount DC power jack by through hole version.
    [shield.brd, shield.sch]
2014-05-06 * pcb/impy: (shield.sch, shield.brd) Revert previous commit 243.
    [shield.brd, shield.sch]
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2014-05-06 * pcb/impy: (shield.brd) Fix some DRC errors and approve the others: they are either too small supply tracks (that are wide enough or can not be made wider, we know they are alright) or clearance err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
    [shield.brd]
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2014-05-08 * pcb/impy: (shield.brd) Swap calibration headers JP13 and JP14 to have both force connections on the outer and sense connections on the inner side of the calibration board. These approved DRC violat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
    [shield.brd]
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2014-05-11 * pcb/impy: (shield.sch) Fix current measurement jumper values.
    [shield.sch]
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2014-05-28 * pcb/impy: (shield.sch) Add analog switch to quickly charge the AD5933 output coupling capacitor. Change feedback resistor values for output attenuator and VCC/2 divider. (shield.brd) Change package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
    [shield.brd, shield.sch]
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2014-06-23 * pcb/impy: (shield.sch, shield.brd) Remove peripheral power switch, this doesn't really work without more effort to prevent current from flowing through STM32 pins to the peripherals. Also, it's not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
    [shield.brd, shield.sch]
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2014-06-24 * pcb/impy: (shield.sch, shield.brd) Add pull up resistors to I2C clock and data lines, the ones on the discovery board are too weak for a nice 400kHz signal.
    [shield.brd, shield.sch]
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
